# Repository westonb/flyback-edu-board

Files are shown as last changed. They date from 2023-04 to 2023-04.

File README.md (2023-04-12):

# flyback-edu-board
A basic flyback converter optimized for teaching educational labs. 
Designed for Stanford's EE 254 and optimized for the JLC assembly service. 

The board is based on the [UC3482B](https://www.onsemi.com/pdf/datasheet/uc3842b-d.pdf) current mode controller IC and provides a regulated 5V output than can be used to charge a phone. 

The board is designed to aid in teaching fundamentals of power electronics, lab techniques, and control theory. 
It is designed with test points on most relevant circuit nodes. 
The primary and secondary current can be measured with the shunt resistors on the PCB, so most work on the board can be done without the use of a current probe. 

In line with the educational goals the board is designed for low cost assembly. The kicad schematic includes LCSC part numbers for assembly at JLC. At 2023 prices a 25 unit build is <$15 with the JLC PCBA service. 

PCB designed in KICAD 6.

## Specifications
|   |   |
| -------- | -------- |
| Input Voltage | 12V - 36V |
| Output Voltage| 5V |
| Output Current | 1.5A |

## Features
- Built in DC and stepped resistive load
- USB A output
- Short and reverse polarity protection
- Output protected from over-voltage due to regulation fault
- Test points on critical circuit nodes
- Switchable between direct and opto-isolated voltage regulation loops

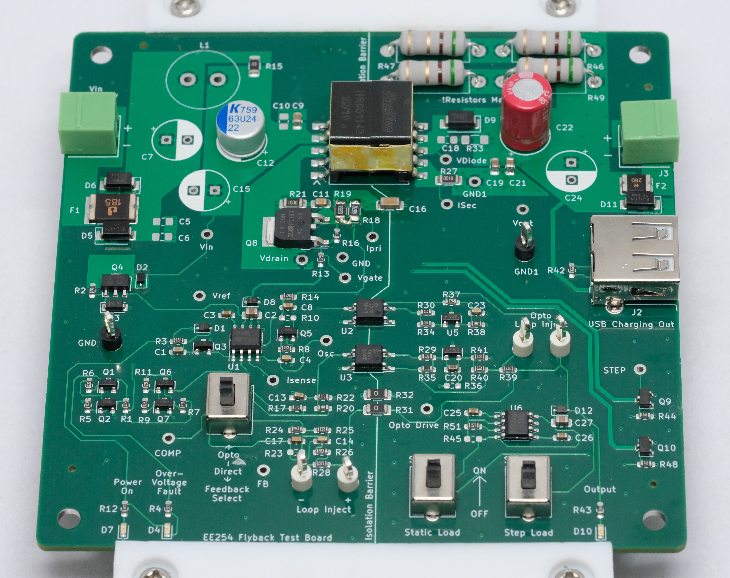
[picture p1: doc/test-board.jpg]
Test Board Photo


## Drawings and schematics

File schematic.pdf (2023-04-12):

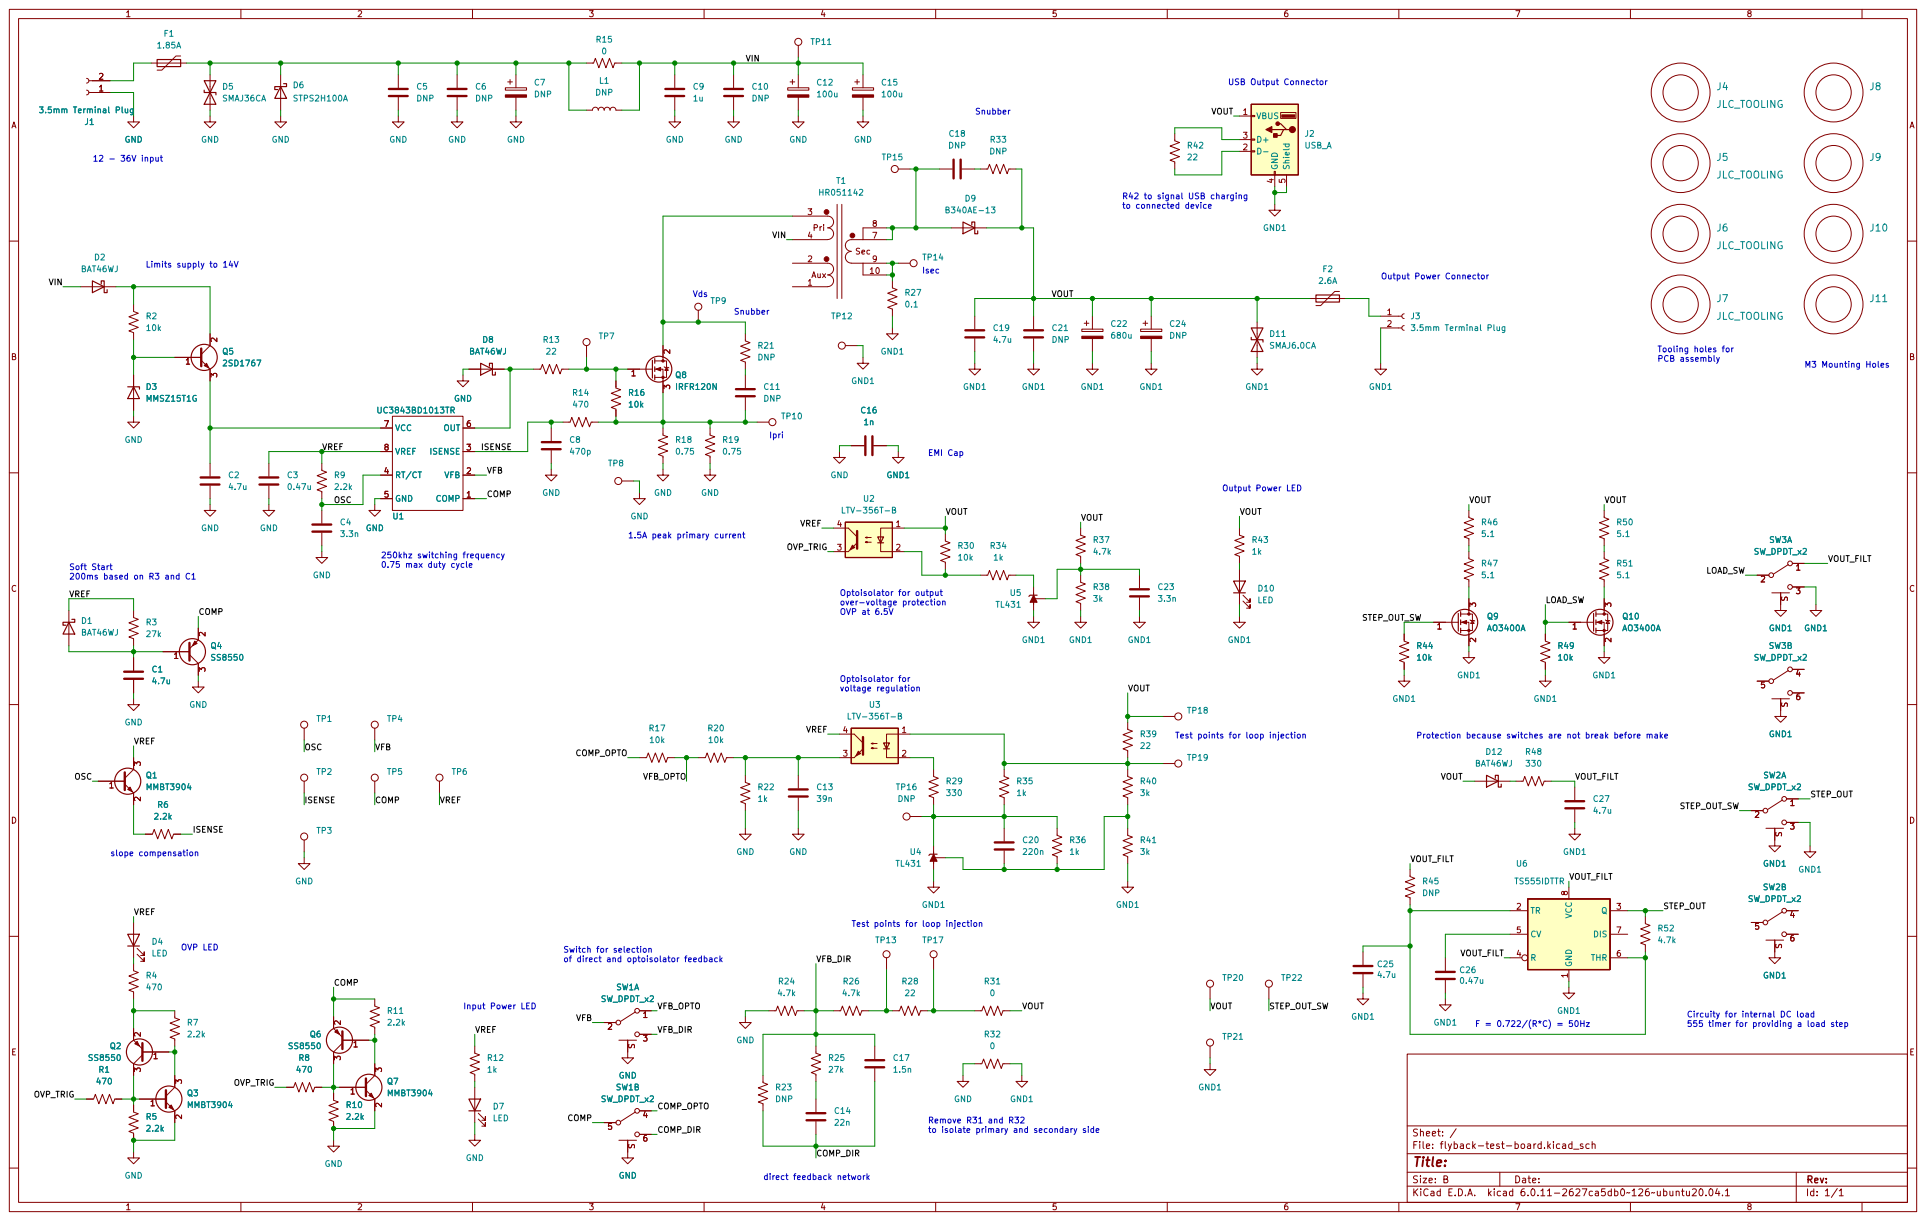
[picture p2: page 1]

Test points for loop injection

Id: 1/1 Title: File: flyback-test-board.kicad_sch Sheet: /

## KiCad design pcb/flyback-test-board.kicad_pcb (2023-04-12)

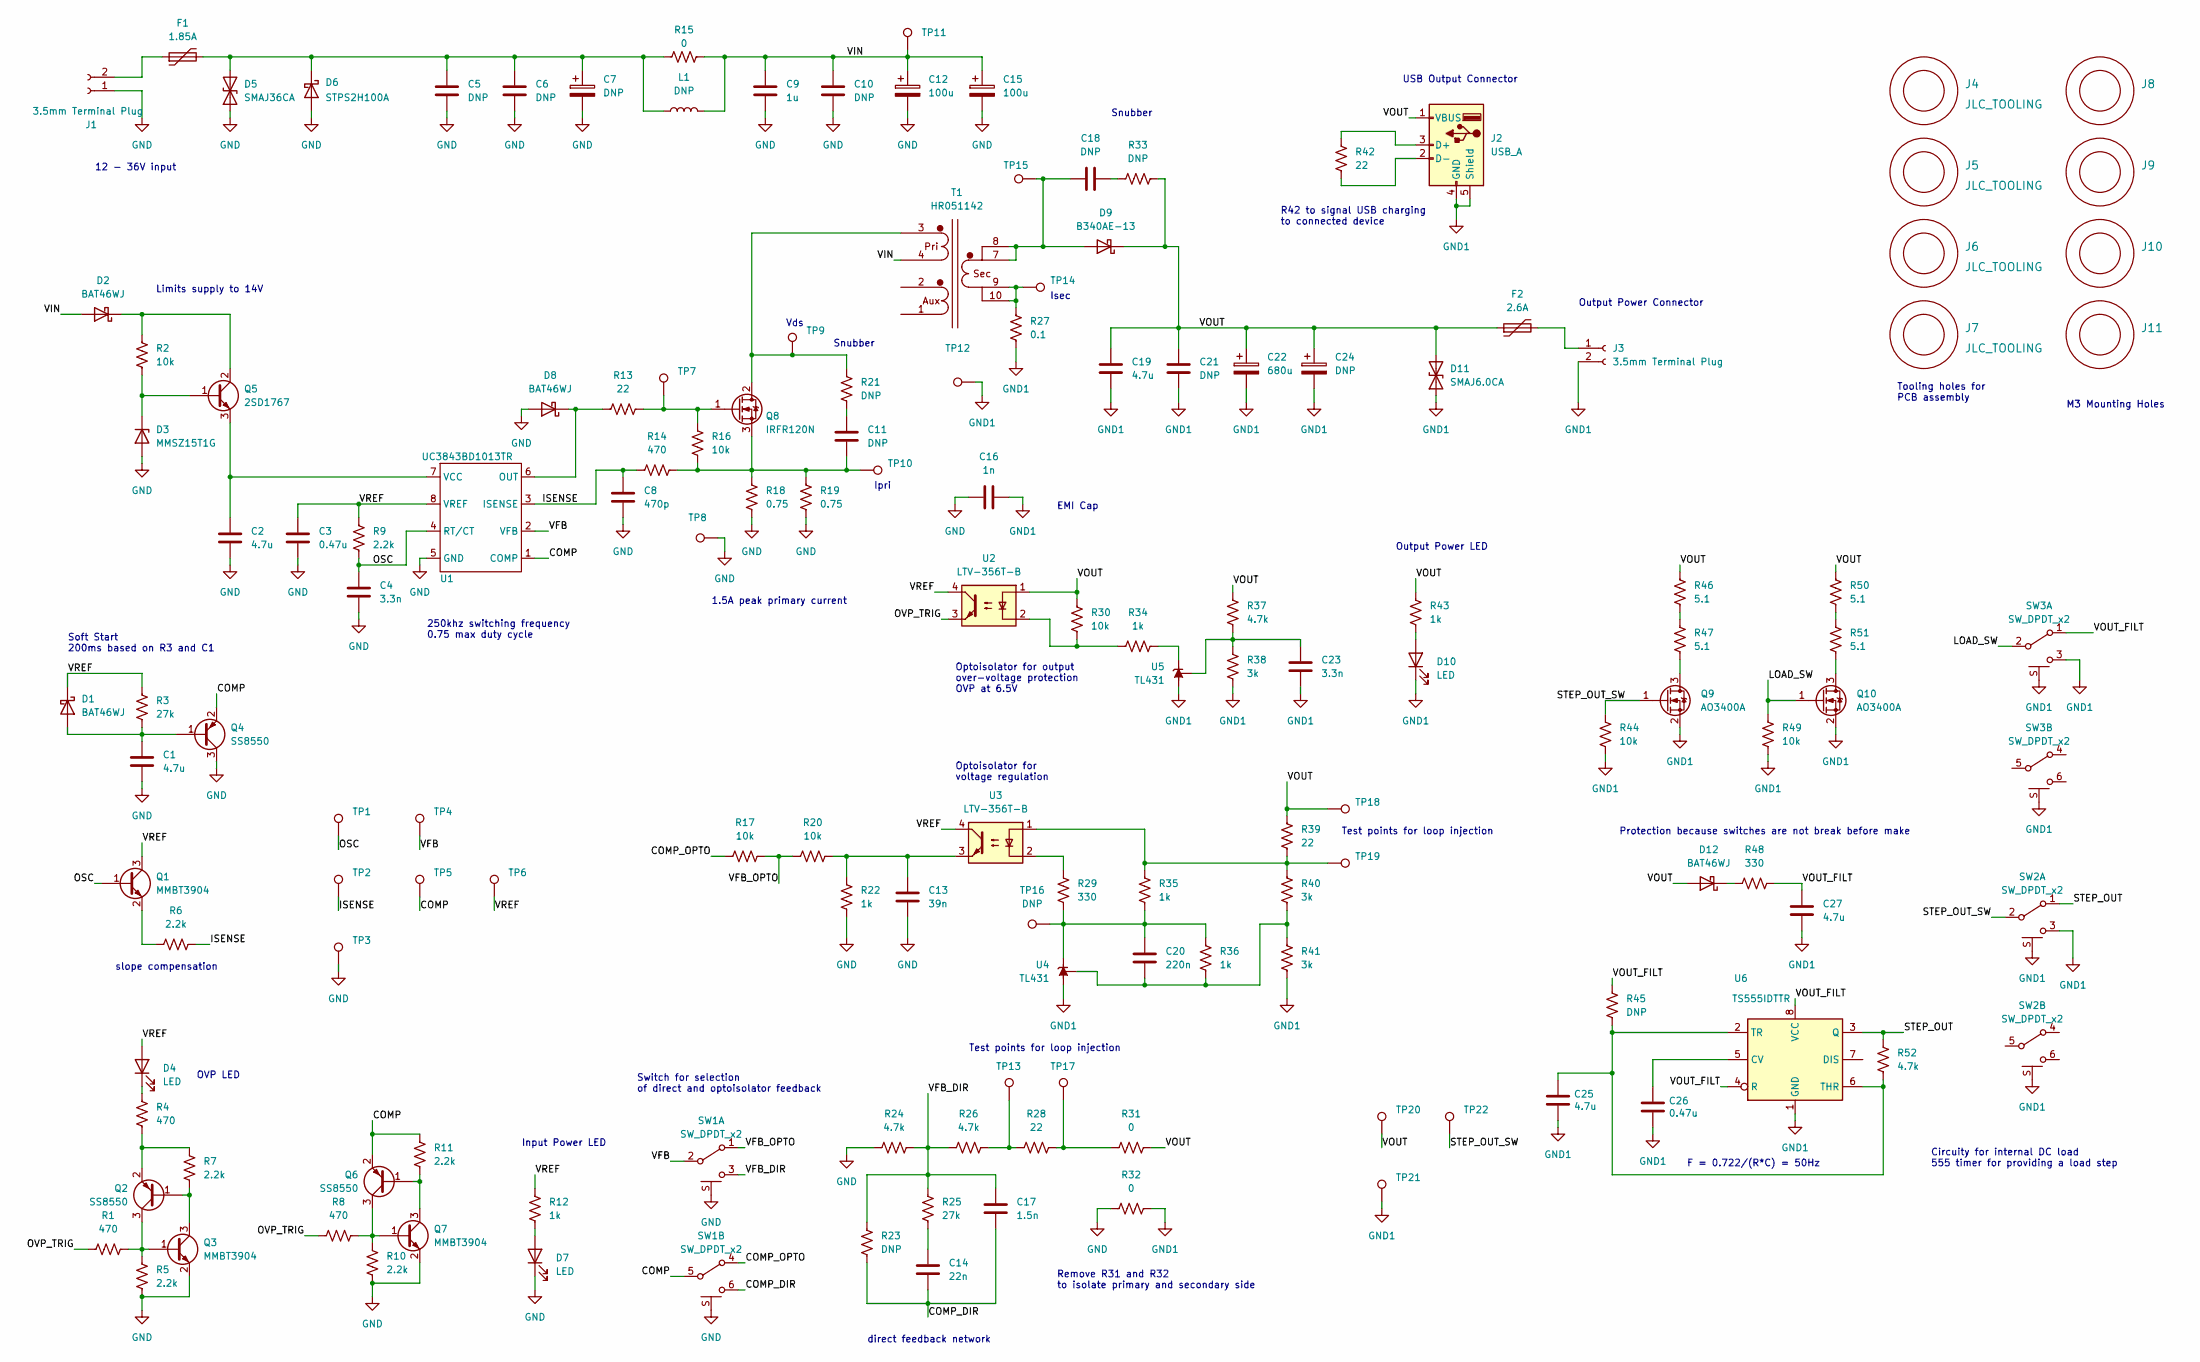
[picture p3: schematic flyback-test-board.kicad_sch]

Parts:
C1: 4.7u; C_0603_1608Metric_Pad1.08x0.95mm_HandSolder; MPN CL10A475KO8NNNC; JLC_MPN C19666
C2, C19, C27: 4.7u; C_0805_2012Metric_Pad1.18x1.45mm_HandSolder; MPN CL21A475KAQNNNE; JLC_MPN C1779
C3, C26: 0.47u; C_0603_1608Metric_Pad1.08x0.95mm_HandSolder; MPN CL10B474KA8NNNC; JLC_MPN C1623
C4, C23: 3.3n; C_0603_1608Metric_Pad1.08x0.95mm_HandSolder; MPN CL10B332KB8NNNC; JLC_MPN C1613
C5, C6, C10, C11, C18, C21: DNP; C_0805_2012Metric_Pad1.18x1.45mm_HandSolder
C7, C24: DNP; CP_Radial_D8.0mm_P3.50mm
C8: 470p; C_0603_1608Metric_Pad1.08x0.95mm_HandSolder; MPN 0603B471K500NT; JLC_MPN C1620
C9: 1u; C_0805_2012Metric_Pad1.18x1.45mm_HandSolder; MPN CL21B105KBFNNNE; JLC_MPN C28323
C12, C15: 100u; CP_Radial_D8.0mm_P3.50mm; MPN 50ZLH100MEFC8X11.5; JLC_MPN C109393
C13: 39n; C_0603_1608Metric_Pad1.08x0.95mm_HandSolder; MPN CC0603KRX7R9BB393; JLC_MPN C107091
C14: 22n; C_0603_1608Metric_Pad1.08x0.95mm_HandSolder; MPN CL10B223KB8NNNC; JLC_MPN C21122
C16: 1n; C_1206_3216Metric_Pad1.33x1.80mm_HandSolder; MPN 1206B102K202NT; JLC_MPN C9196
C17: 1.5n; C_0603_1608Metric_Pad1.08x0.95mm_HandSolder; MPN 0603B152K500NT; JLC_MPN C1595
C20: 220n; C_0603_1608Metric_Pad1.08x0.95mm_HandSolder; MPN GCM188R71H224KA64D; JLC_MPN C97857
C22: 680u; CP_Radial_D8.0mm_P3.50mm; MPN 16ZLH680MEFC8X16; JLC_MPN C88760
C25: 4.7u; C_0603_1608Metric_Pad1.08x0.95mm_HandSolder
D1, D2, D8, D12: BAT46WJ; D_SOD-323; MPN BAT46WJ,115; JLC_MPN C114696
D3: MMSZ15T1G; D_SOD-123; MPN MMSZ15T1G; JLC_MPN C27754
D4, D7, D10: LED; LED_0603_1608Metric; MPN 19-213/Y2C-CQ2R2L/3T(CY); JLC_MPN C72038
D5: SMAJ36CA; D_SMA; MPN SMAJ36CA/TR13; JLC_MPN C87270
D6: STPS2H100A; D_SMA; MPN STPS2H100A; JLC_MPN C81548
D9: B340AE-13; D_SMA; MPN B340AE-13; JLC_MPN C168859
D11: SMAJ6.0CA; D_SMA; MPN SMAJ6.0CA; JLC_MPN C10759
F1: 1.85A; Fuse_2920_7451Metric; MPN ASMD2920-185; JLC_MPN C135379
F2: 2.6A; Fuse_1812_4532Metric; MPN SMD1812P260TF/16; JLC_MPN C20814
J1, J3: 3.5mm Terminal Plug; Terminal-block-plug_2x1_3.5mm-pitch; MPN XY2500R-G-3.5-2P; JLC_MPN C880572
J2: USB_A; USB_A_Stewart_SS-52100-001_Horizontal; MPN 902-141A1011D10100; JLC_MPN C42643
J4, J5, J6, J7: JLC_TOOLING; JLC_TOOLING_HOLE
J8, J9, J10, J11: DNP; M3-mounting-hole-insulated
L1: DNP; L_Radial_D12.0mm_P5.00mm_Fastron_11P
Q1, Q3, Q7: MMBT3904; SOT-23; MPN MMBT3904; JLC_MPN C20526
Q2, Q4, Q6: SS8550; SOT-23; MPN SS8550; JLC_MPN C8542
Q5: 2SD1767; SOT-89-3; MPN 2SD1767T100Q; JLC_MPN C24250
Q8: IRFR120N; TO-252-2; MPN IRFR120NTRPBF; JLC_MPN C3008
Q9, Q10: AO3400A; SOT-23; MPN AO3400A; JLC_MPN C20917
R1, R4, R8, R14: 470; R_0603_1608Metric_Pad0.98x0.95mm_HandSolder; MPN 0603WAF4700T5E; JLC_MPN C23179
R2, R16, R17, R20, R30, R44, R49: 10k; R_0603_1608Metric_Pad0.98x0.95mm_HandSolder; MPN 0603WAF1002T5E; JLC_MPN C25804
R3, R25: 27k; R_0603_1608Metric_Pad0.98x0.95mm_HandSolder; MPN 0603WAF2702T5E; JLC_MPN C22967
R5, R6, R7, R9, R10, R11: 2.2k; R_0603_1608Metric_Pad0.98x0.95mm_HandSolder; MPN 0603WAF2201T5E; JLC_MPN C4190
R12, R22, R34, R35, R36, R43: 1k; R_0603_1608Metric_Pad0.98x0.95mm_HandSolder; MPN 0603WAF1001T5E; JLC_MPN C21190
R13, R28, R39, R42: 22; R_0603_1608Metric_Pad0.98x0.95mm_HandSolder; MPN 0603WAF220JT5E; JLC_MPN C23345
R15, R31, R32: 0; R_1206_3216Metric_Pad1.30x1.75mm_HandSolder; MPN 1206W4F0000T5E; JLC_MPN C17888
R18, R19: 0.75; R_1206_3216Metric_Pad1.30x1.75mm_HandSolder; MPN FRL1206FR750TS; JLC_MPN C2907360
R21, R33: DNP; R_1206_3216Metric_Pad1.30x1.75mm_HandSolder
R23, R45: DNP; R_0603_1608Metric_Pad0.98x0.95mm_HandSolder
R24, R26, R37, R52: 4.7k; R_0603_1608Metric_Pad0.98x0.95mm_HandSolder; MPN 0603WAF4701T5E; JLC_MPN C23162
R27: 0.1; R_1206_3216Metric_Pad1.30x1.75mm_HandSolder; MPN 1206W4F100LT5E; JLC_MPN C25334
R29, R48: 330; R_0603_1608Metric_Pad0.98x0.95mm_HandSolder; MPN 0603WAF3300T5E; JLC_MPN C23138
R38, R40, R41: 3k; R_0603_1608Metric_Pad0.98x0.95mm_HandSolder; MPN 0603WAF3001T5E; JLC_MPN C4211
R46, R47, R50, R51: 5.1; R_Axial_DIN0414_L11.9mm_D4.5mm_P15.24mm_Horizontal; MPN MOF2WS-5.1Ω±5% T; JLC_MPN C121605
SW1, SW2, SW3: SW_DPDT_x2; Switch_DPDT_OS202011MS2QS1; MPN SS22D03L5; JLC_MPN C609823
T1: HR051142; Transformer_POE13P; MPN HR051142; JLC_MPN C55680
TP1, TP2, TP4, TP5, TP6, TP7, TP8, TP9, TP10, TP11, TP12, TP14, TP15, TP16, TP20, TP22: DNP; THM_MINI
TP3, TP21: 5011; THM_COMPACT; MPN 5011; JLC_MPN C238127
TP13, TP17, TP18, TP19: RH-5012; THM_COMPACT; MPN RH-5012; JLC_MPN C5199815
U1: UC3843BD1013TR; SO-8_3.9x4.9mm_P1.27mm; MPN UC3843BD1013TR; JLC_MPN C92746
U2, U3: LTV-356T-B; SO-4_4.4x3.6mm_P2.54mm; MPN LTV-356T-B; JLC_MPN C10804
U4, U5: TL431; SOT-23; MPN TL431AFDT,215; JLC_MPN C97758
U6: TS555IDTTR; SOIC-8_3.9x4.9mm_P1.27mm; MPN TS555IDTTR; JLC_MPN C880084

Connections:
/COMP: Q4.2 (E), Q6.2 (E), R11.1, SW1.5 (B), TP5.1, U1.1 (COMP)
/COMP_DIR: C14.2, C17.2, R23.2, SW1.6 (C)
/COMP_OPTO: R17.2, SW1.4 (A)
/ISENSE: C8.1, R6.1, R14.2, TP2.1, U1.3 (ISENSE)
/LOAD_SW: Q10.1 (G), R49.2, SW3.2 (B)
/OSC: C4.1, Q1.1 (B), R9.2, TP1.1, U1.4 (RT/CT)
/OVP_TRIG: R1.1, R8.1, U2.3
/STEP_OUT: R52.1, SW2.1 (A), U6.3 (Q)
/STEP_OUT_SW: Q9.1 (G), R44.2, SW2.2 (B), TP22.1
/VFB: SW1.2 (B), TP4.1, U1.2 (VFB)
/VFB_DIR: C17.1, R23.1, R24.1, R25.1, R26.2, SW1.3 (C)
/VFB_OPTO: R17.1, R20.2, SW1.1 (A)
/VIN: C9.1, C10.1, C12.1, C15.1, D2.2 (A), L1.2, R15.2, T1.4 (Pri_M), TP11.1
/VOUT: C19.1, C21.1, C22.1, C24.1, D9.1 (K), D11.2 (A2), D12.2 (A), F2.1, J2.1 (VBUS), R30.2, R31.1, R33.1, R37.2, R39.1, R43.2, R46.1, R50.1, TP18.1, TP20.1, U2.1
/VOUT_FILT: C27.1, R45.1, R48.2, SW3.1 (A), U6.4 (R), U6.8 (VCC)
/VREF: C3.1, D1.1 (K), D4.2 (A), Q1.3 (C), R3.1, R9.1, R12.2, TP6.1, U1.8 (VREF), U2.4, U3.4
GND: C1.2, C2.2, C3.2, C4.2, C5.2, C6.2, C7.2, C8.2, C9.2, C10.2, C12.2, C13.2, C15.2, C16.1, D3.2 (A), D5.1 (A1), D6.2 (A), D7.1 (K), D8.2 (A), J1.1, Q3.2 (E), Q4.3 (C), Q7.2 (E), R5.2, R10.2, R18.1, R19.1, R22.1, R24.2, R32.2, SW1.S, TP3.1, TP8.1, U1.5 (GND)
GND1: C16.2, C19.2, C21.2, C22.2, C23.2, C24.2, C25.1, C26.1, C27.2, D10.1 (K), D11.1 (A1), J2.4 (GND), J2.5 (Shield), J3.2, Q9.2 (S), Q10.2 (S), R27.2, R32.1, R38.1, R41.2, R44.1, R49.1, SW2.3 (C), SW2.S, SW3.3 (C), SW3.S, TP12.1, TP21.1, U4.3 (A), U5.3 (A), U6.1 (GND)
unnamed: C1.1, D1.2 (A), Q4.1 (B), R3.2
unnamed: C2.1, Q5.3 (E), U1.7 (VCC)
unnamed: C5.1, C6.1, C7.1, D5.2 (A2), D6.1 (K), F1.2, L1.1, R15.1
unnamed: C11.1, R21.1
unnamed: C11.2, Q8.3 (S), R14.1, R16.1, R18.2, R19.2, TP10.1
unnamed: C13.1, R20.1, R22.2, U3.3
unnamed: C14.1, R25.2
unnamed: C18.1, D9.2 (A), T1.7 (SEC_P), T1.8 (SEC_P), TP15.1
unnamed: C18.2, R33.2
unnamed: C20.1, R29.2, R35.2, R36.1, TP16.1, U4.1 (K)
unnamed: C20.2, R36.2, R40.2, R41.1, U4.2 (REF)
unnamed: C23.1, R37.1, R38.2, U5.2 (REF)
unnamed: C25.2, R45.2, R52.2, U6.2 (TR), U6.6 (THR)
unnamed: C26.2, U6.5 (CV)
unnamed: D2.1 (K), Q5.2 (C), R2.1
unnamed: D3.1 (K), Q5.1 (B), R2.2
unnamed: D4.1 (K), R4.1
unnamed: D7.2 (A), R12.1
unnamed: D8.1 (K), R13.1, U1.6 (OUT)
unnamed: D10.2 (A), R43.1
unnamed: D12.1 (K), R48.1
unnamed: F1.1, J1.2
unnamed: F2.2, J3.1
unnamed: J2.2 (D-), R42.1
unnamed: J2.3 (D+), R42.2
unnamed: Q1.2 (E), R6.2
unnamed: Q2.1 (B), Q3.3 (C), R7.2
unnamed: Q2.2 (E), R4.2, R7.1
unnamed: Q2.3 (C), Q3.1 (B), R1.2, R5.1
unnamed: Q6.1 (B), Q7.3 (C), R11.2
unnamed: Q6.3 (C), Q7.1 (B), R8.2, R10.1
unnamed: Q8.1 (G), R13.2, R16.2, TP7.1
unnamed: Q8.2 (D), R21.2, T1.3 (Pri_P), TP9.1
unnamed: Q9.3 (D), R47.2
unnamed: Q10.3 (D), R51.2
unnamed: R26.1, R28.2, TP13.1
unnamed: R27.1, T1.9 (SEC_M), T1.10 (SEC_M), TP14.1
unnamed: R28.1, R31.2, TP17.1
unnamed: R29.1, U3.2
unnamed: R30.1, R34.2, U2.2
unnamed: R34.1, U5.1 (K)
unnamed: R35.1, R39.2, R40.1, TP19.1, U3.1
unnamed: R46.2, R47.1
unnamed: R50.2, R51.1

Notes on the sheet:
Limits supply to 14V
M3 Mounting Holes
Snubber
F = 0.722/(R*C) = 50Hz
250khz switching frequency 0.75 max duty cycle
slope compensation
Ipri
EMI Cap
Isec
Test points for loop injection
R42 to signal USB charging to connected device
direct feedback network
Protection because switches are not break before make
Circuity for internal DC load 555 timer for providing a load step
Output Power LED
Input Power LED
Tooling holes for PCB assembly
1.5A peak primary current
Switch for selection of direct and optoisolator feedback
Output Power Connector
Vds
Remove R31 and R32 to isolate primary and secondary side
Soft Start 200ms based on R3 and C1
OVP LED
12 - 36V input
Optoisolator for voltage regulation
Optoisolator for output over-voltage protection OVP at 6.5V
USB Output Connector

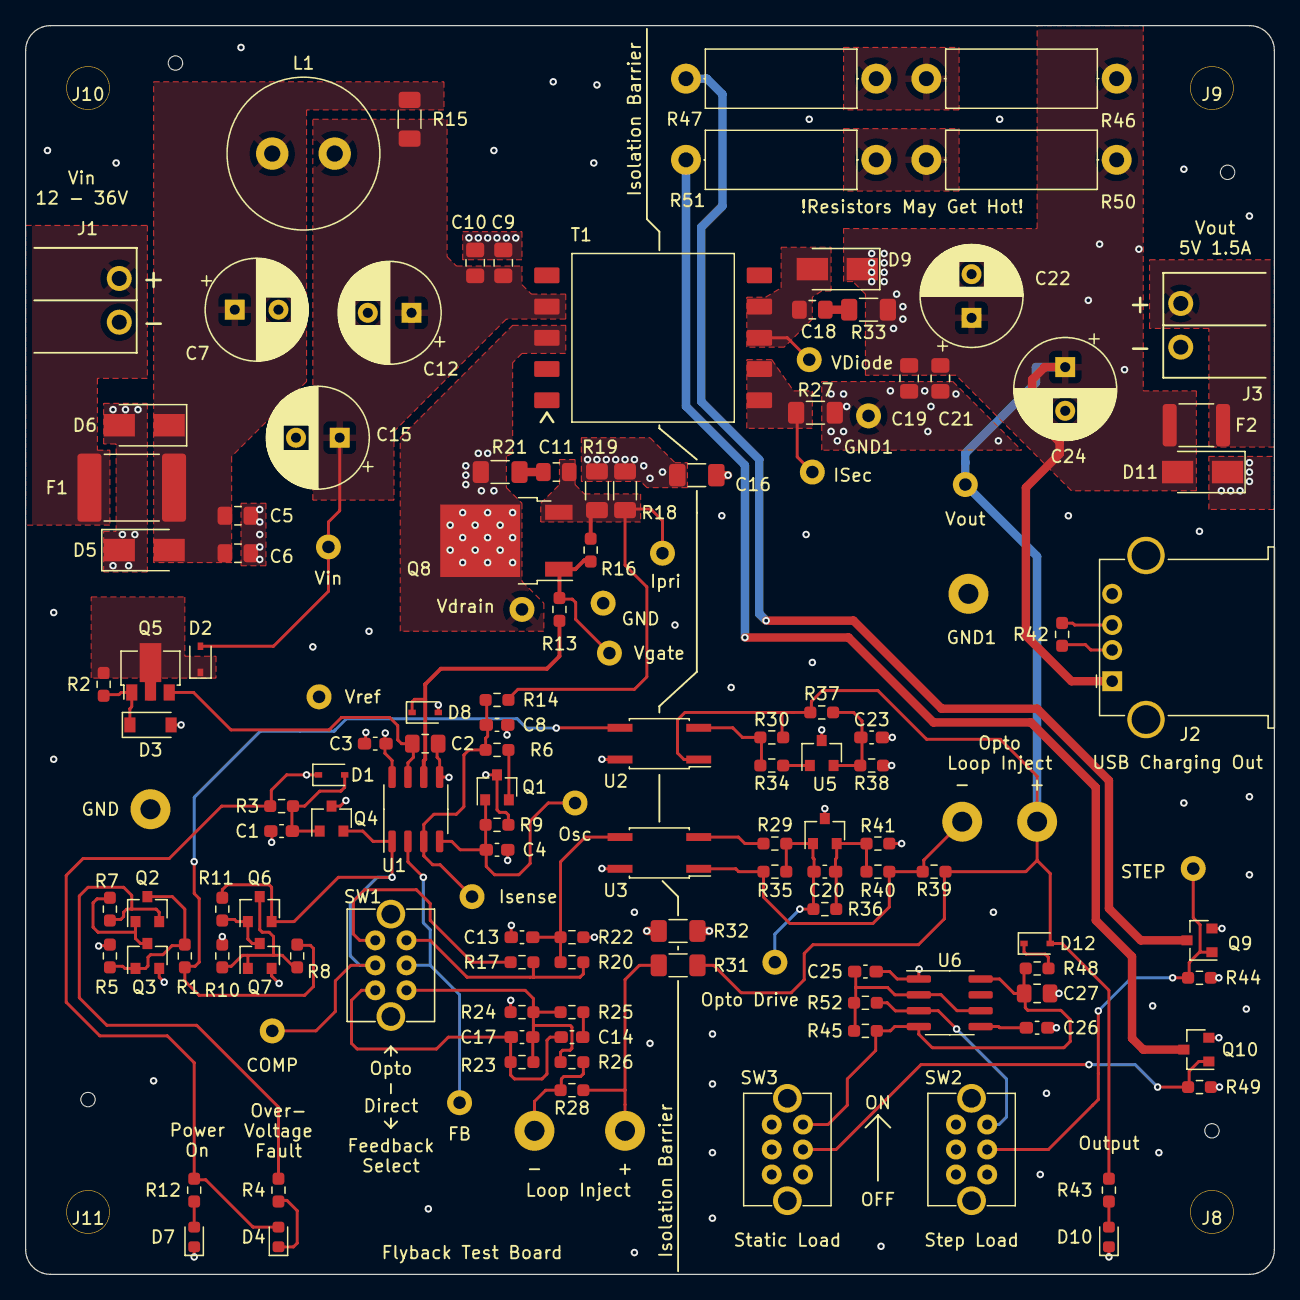
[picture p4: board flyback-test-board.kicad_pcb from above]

Board: 4 copper layers, 100.0 x 100.0 mm, 147 parts (0 on the bottom side), 62 nets.
